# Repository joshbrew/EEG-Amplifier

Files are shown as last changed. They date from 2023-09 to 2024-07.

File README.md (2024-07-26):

## EEG Differential Amplifier

The main circuit here uses 4 low noise op amps to achieve EEG differential amplification. This should plug into any single ended ADC (or put your negative input to ground) to allow even as low as 10 bit EEG.

The amps cost 10 cents from TI, not including the PCB which will vary.

The reference design is for 1000x gain at 5v with a 2.5v voltage reference. All calculations are in the pdf for your needs.

### Resources
- [Differential Amp BOM](https://docs.google.com/spreadsheets/d/1rzFOKtwm5F1gYTblCt51H4664hxHK5iFGmpR6K0Omsg/edit?usp=sharing)
- [Gain Amp BOM](https://docs.google.com/spreadsheets/d/1fu1xdZPcOAWwaKk6sFUOHw02OROvW1wCZvjth2xU8xA/edit?usp=sharing)
- [Design reference](https://github.com/joshbrew/EEG-Amplifier/blob/main/EEG_Active_electrode_design.pdf) by Abishek Parikh. 
Other info pulled from datasheets.

Note my previous OPA202 config was incorrect. And use this formula for calculating the bandpass: 
<table>
  <tr>
    <td>
      <br/>
      In our config, + is our reference <br/> 
      (e.g. ear for EEG or opposite wrist for ECG)
    </td>
    <td>
      
    </td>
    <td>
      Gain = R2 / R1
    </td>
  </tr>
</table>

### OPA4202ID/TL084CDR/TL084OD (or compatible SOIC14) SMT mount.
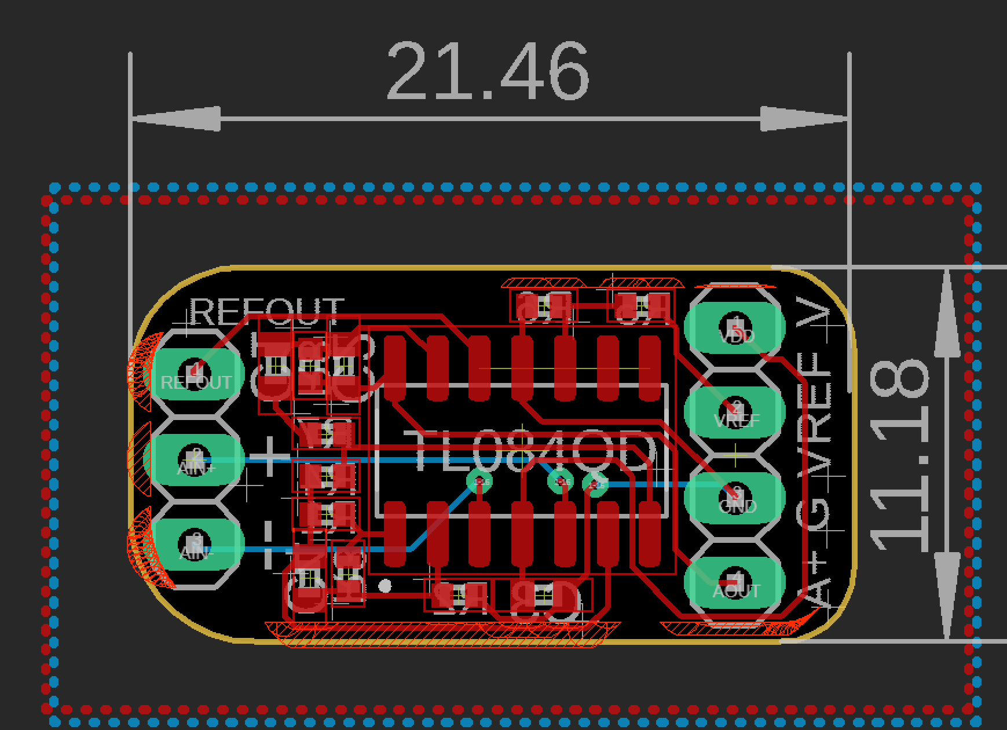
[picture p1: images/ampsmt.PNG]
amp2

OPA4202ID is more expensive but MUCH better quality, with better input impedance (3TΩ) and a 9nV/sqrt(Hz) noise density starting at 0.1Hz. The TL084's spectral noise doesn't bottom out until near 1kHz.

### 4mm Snap Button Electrode Mountholes
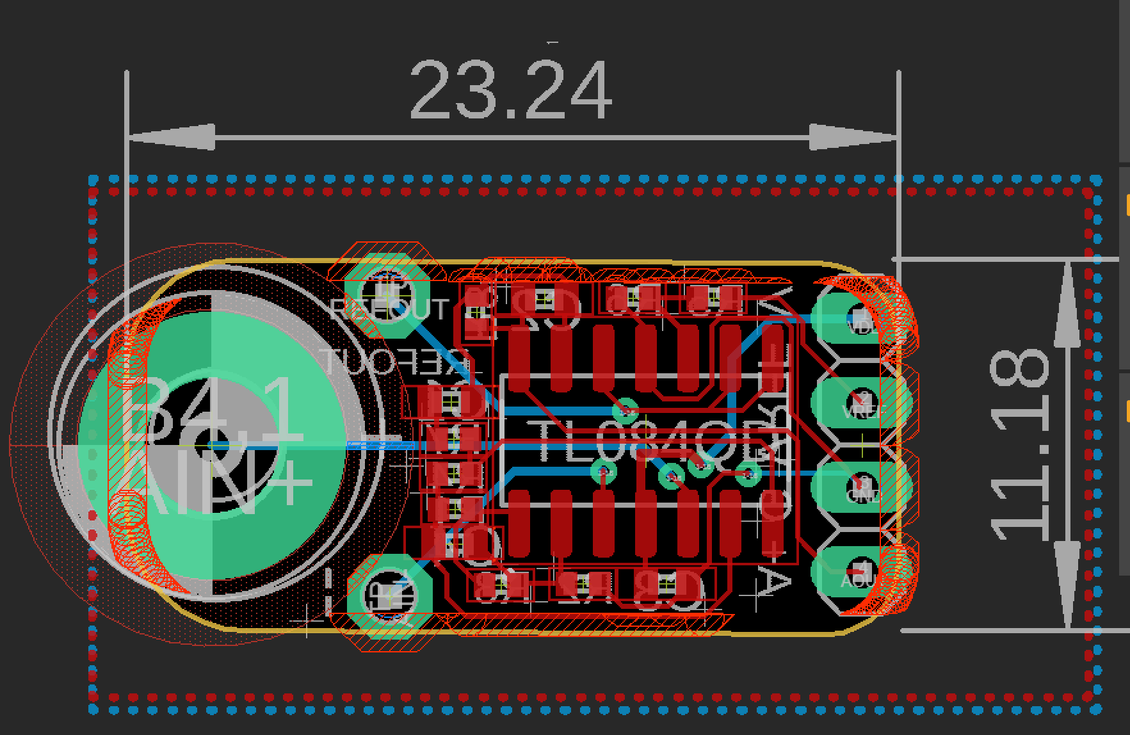
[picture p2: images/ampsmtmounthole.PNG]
amp2mount

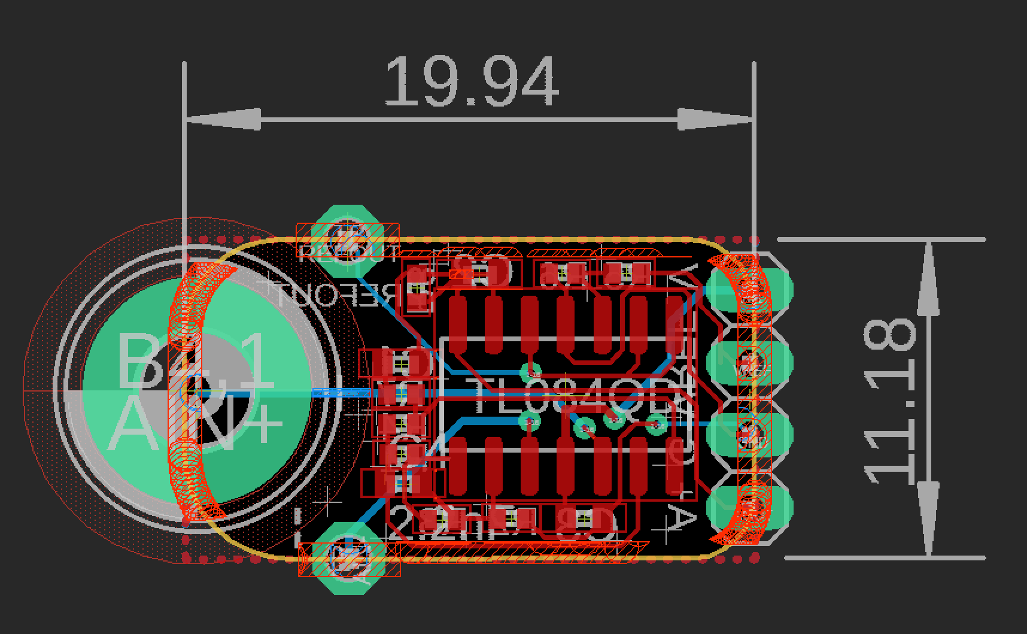
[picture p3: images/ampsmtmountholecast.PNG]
amp2mountCast

Sized for Florida Instruments reusable plastic snap electrodes.

### TL084HCN (A,B,H, etc) Thruhole amp (for DIY)
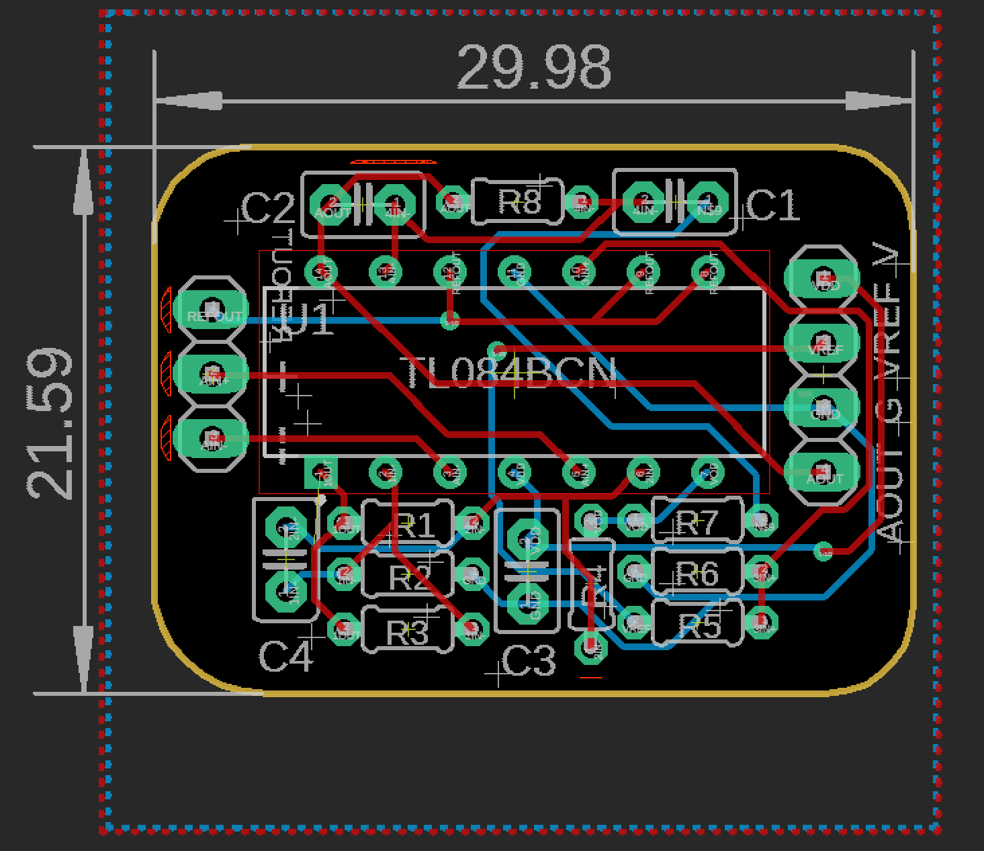
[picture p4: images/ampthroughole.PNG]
amp


### OPA4202IPW or OPA4377 (or  compatible TSSOP14) SMT mount.
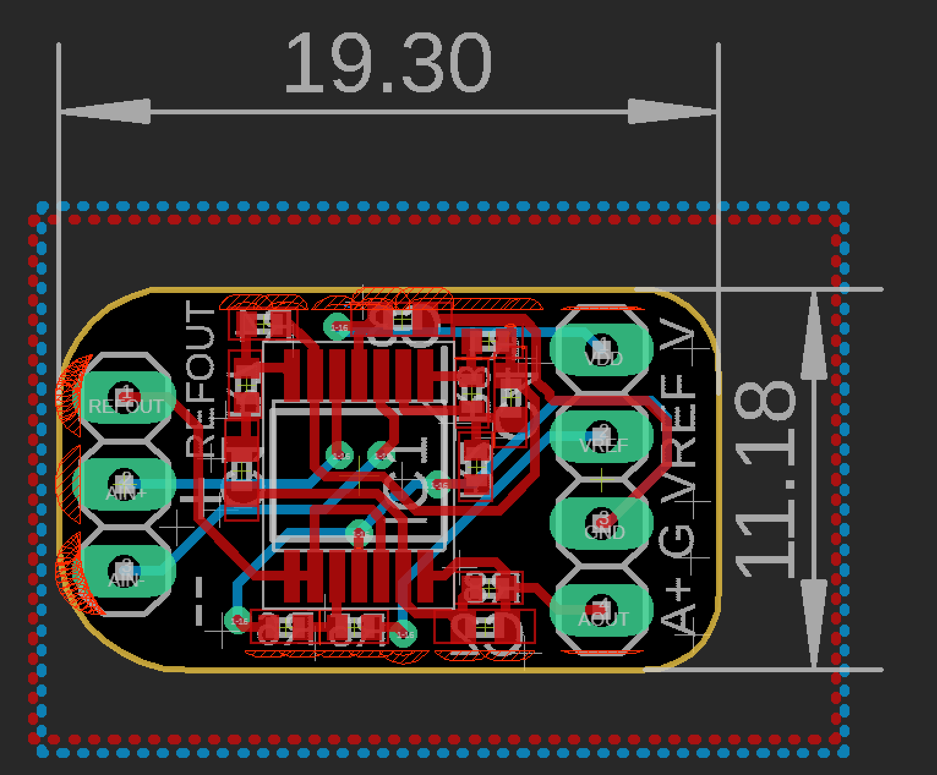
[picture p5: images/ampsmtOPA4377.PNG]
amp3


### Schematics
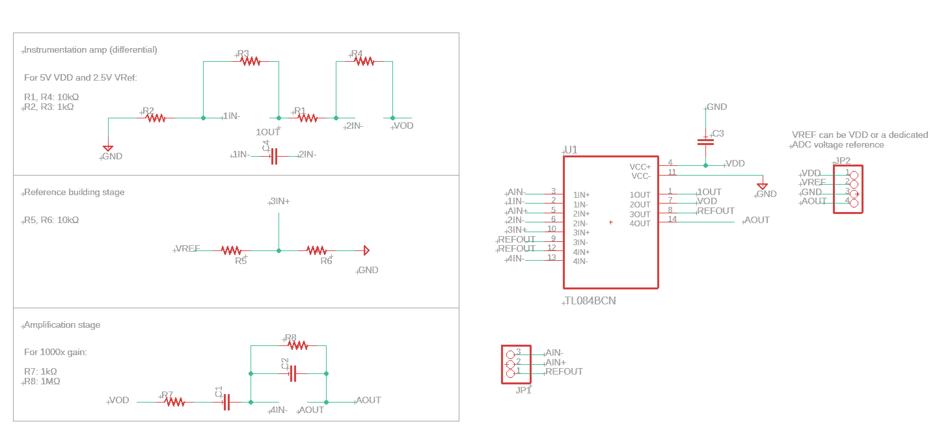
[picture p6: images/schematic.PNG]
schem

The BioAmp EXG Pill has a different layout you can check out. Same chipset.

### Noise vs Measured Bandwidth on OPA4202
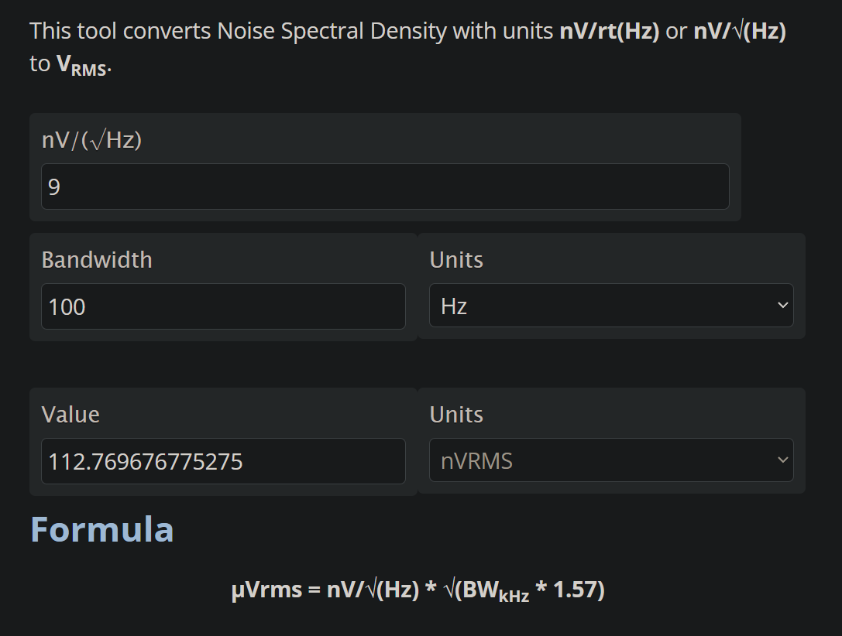
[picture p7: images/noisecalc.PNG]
calcs

Note: Noise calcs are probably inaccurate. Lower frequencies have higher noise density. Adjust bandpass accordingly.

TL084 noise density:
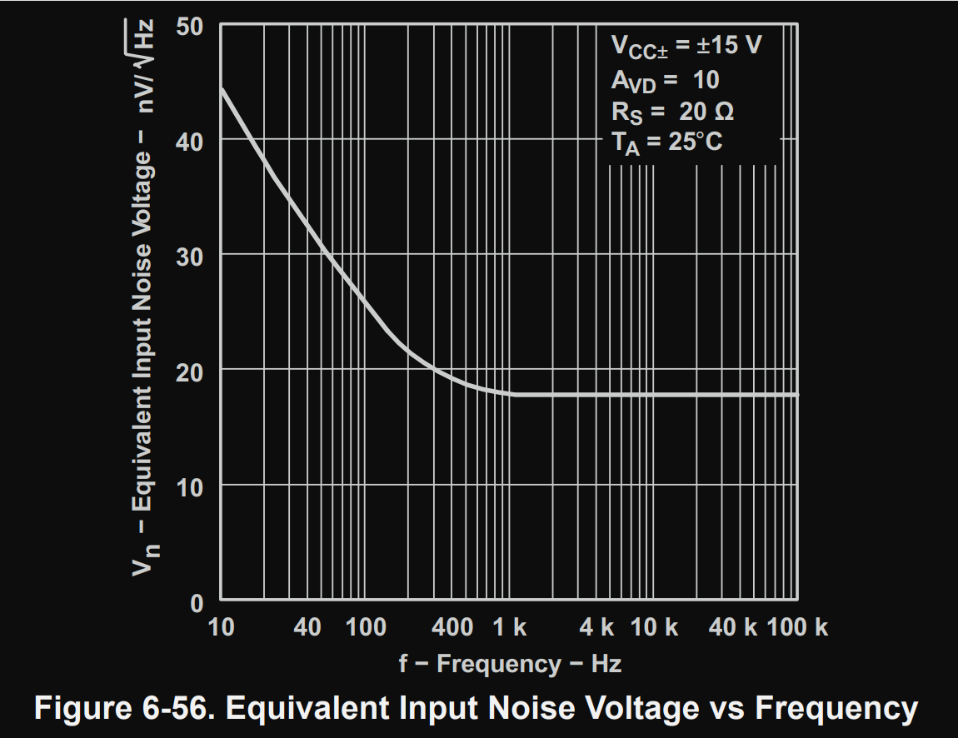
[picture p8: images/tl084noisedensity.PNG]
density


OPA4202 noise density:
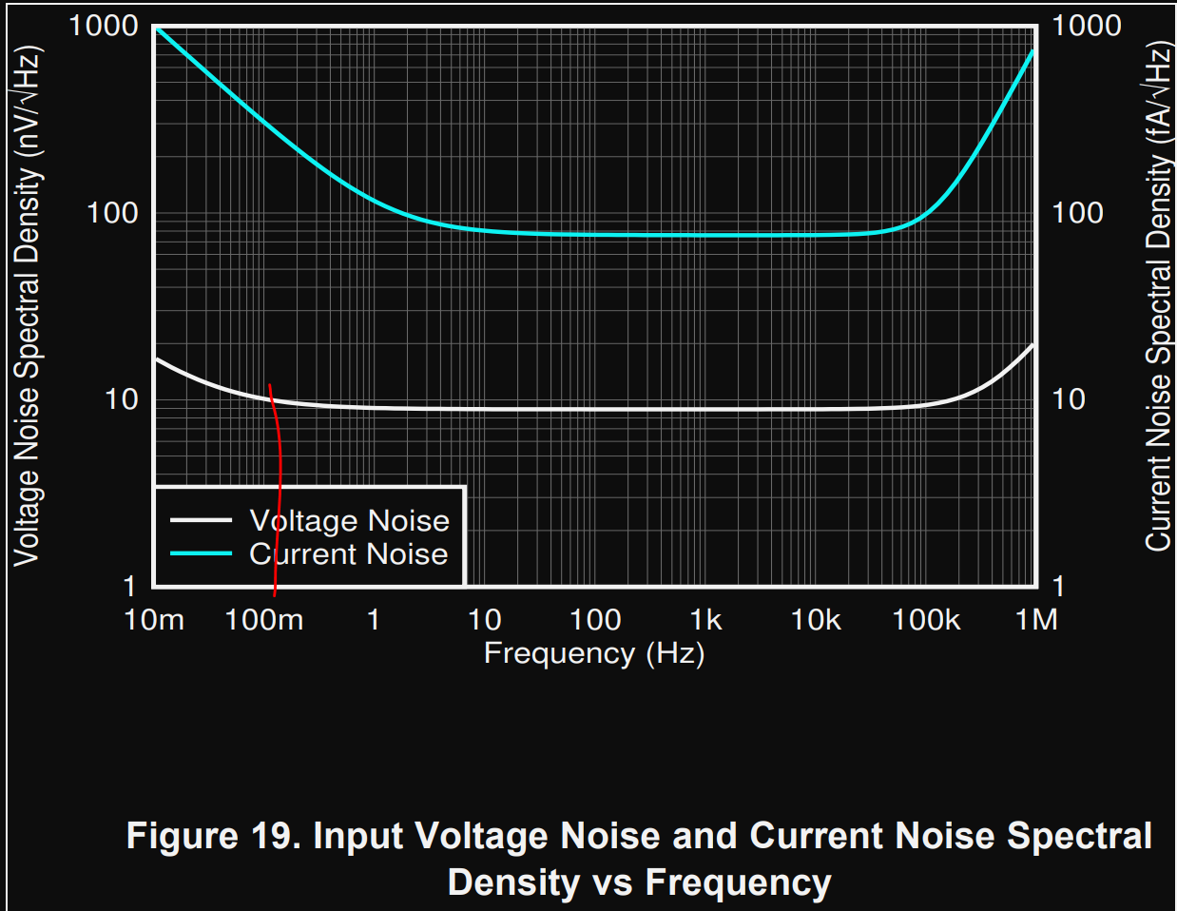
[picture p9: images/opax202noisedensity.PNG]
density2


OPA4202 or OPA4377 are about a dollar. I think the 4202 is better based on the noise.

## Also included in CAD/singular_amps

Single and Dual OPA202/OPA2202 gain amplifiers. E.g. for pre-amplification. Great low frequency noise density. 
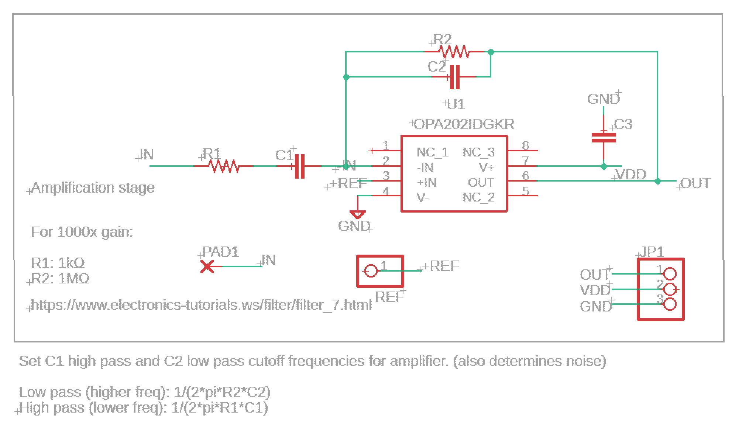
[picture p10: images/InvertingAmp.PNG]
gain


### OPA202 (or pin compatible) VSSOP8 package (or pin compatible)
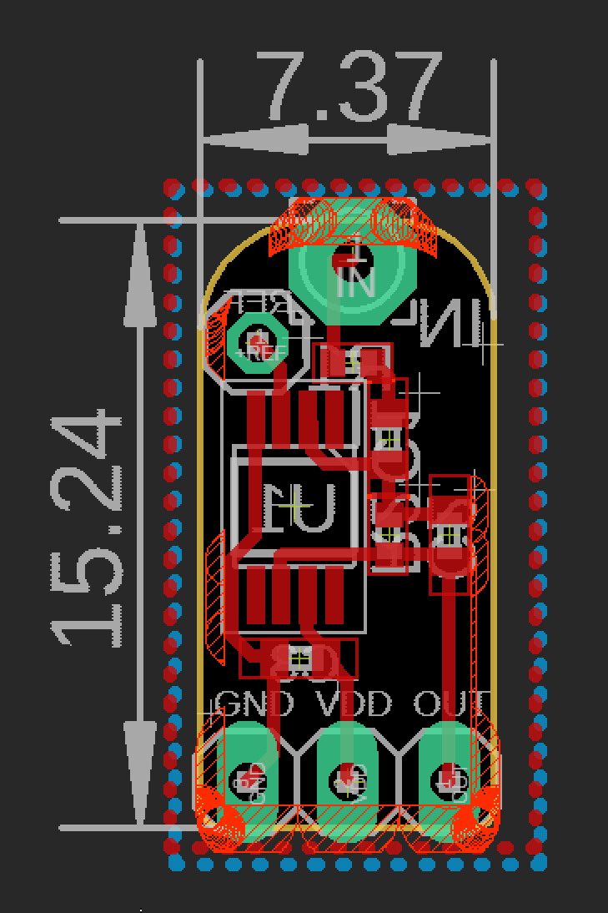
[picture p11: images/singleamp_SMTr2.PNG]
smtgain


### OPA202 VSSOP8 package with 4mm electrode mount
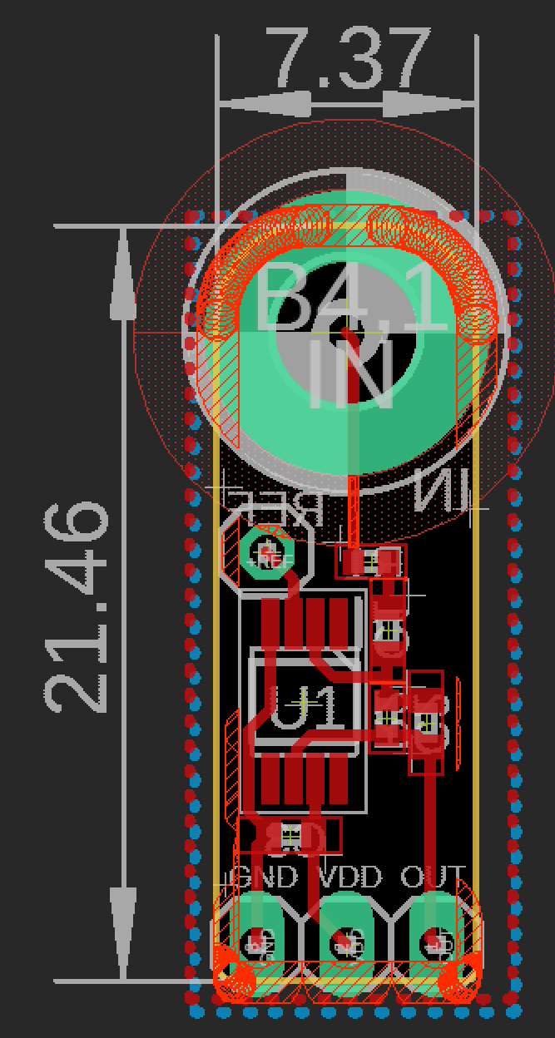
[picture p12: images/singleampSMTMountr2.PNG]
smtgain2


### OPA202 SOIC8 package and thruhole resistors/capacitors (easier to hand solder)
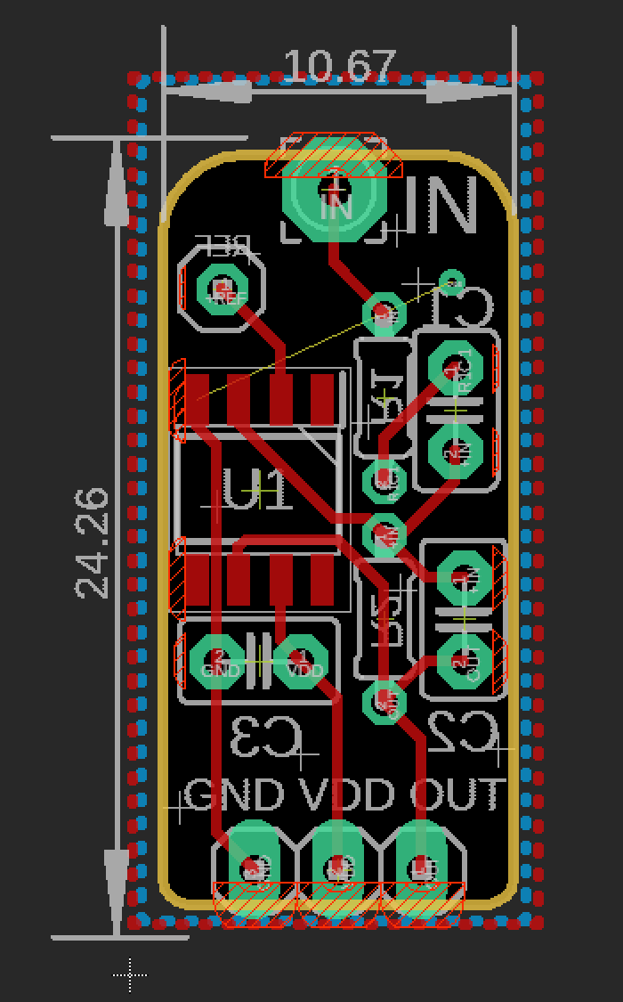
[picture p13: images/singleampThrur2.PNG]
smtgain3


### OPA202 SOIC8 package thruhole with 4mm electrode mount
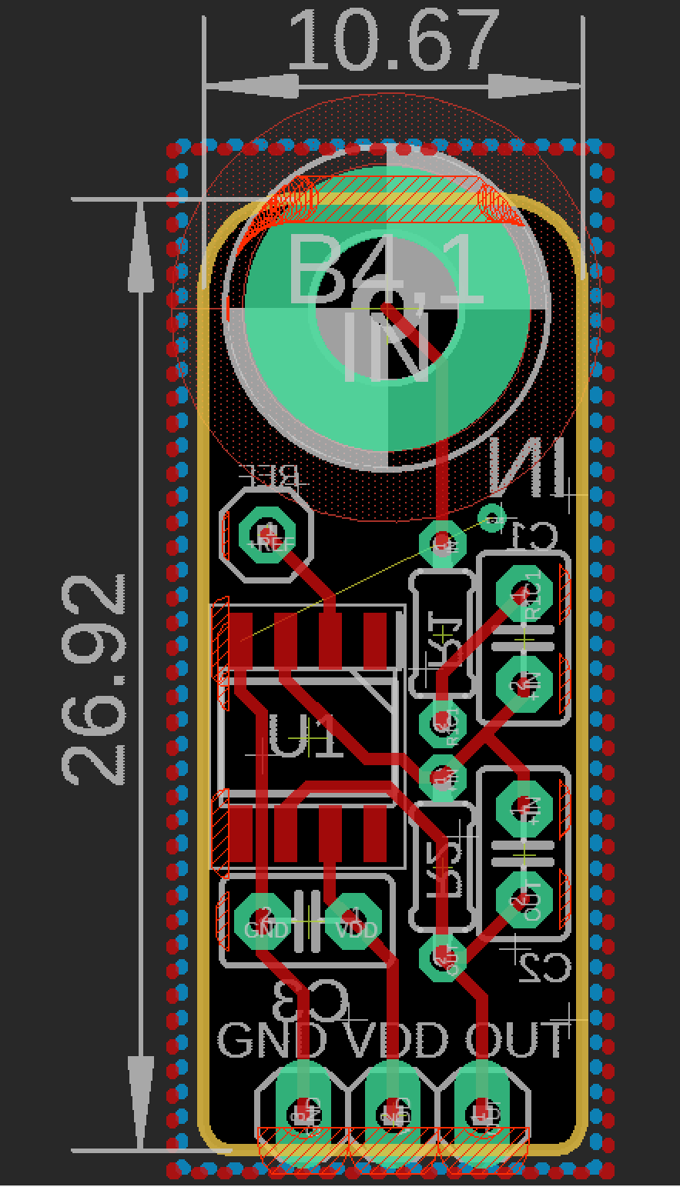
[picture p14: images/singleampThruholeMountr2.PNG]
smtgain4


EAGLE drawings by Josh Brewster. Works in free EAGLE or you can import them elsewhere usually.

Best prices are on TI.com just FYI...

Free source! Definitely question my circuitry before you use it.

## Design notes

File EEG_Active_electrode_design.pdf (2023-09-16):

## Hardware design EEG Amplifier circuit

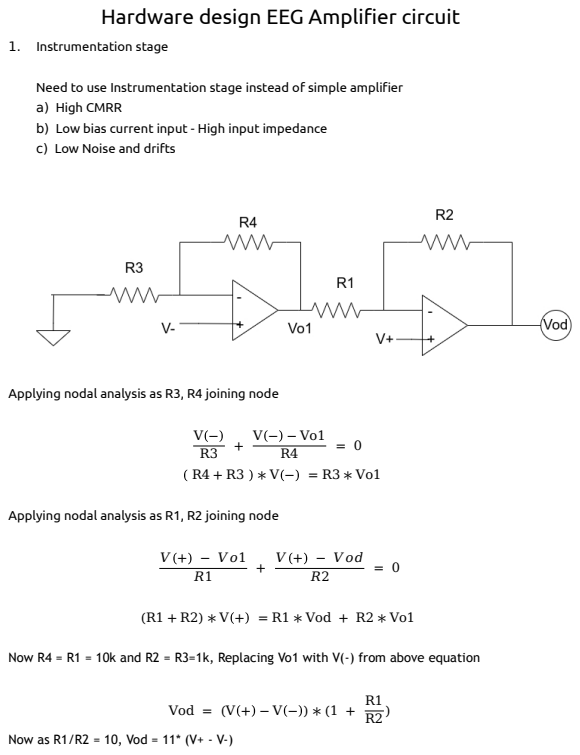
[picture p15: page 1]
1. Instrumentation stage;  + −  2 = 0 (R1 + R2) ∗ V + = R1 ∗ Vod + R2 ∗ Vo1; Vod = (V + − V − ) ∗ (1 +

Need to use Instrumentation stage instead of simple amplifier
a) High CMRR
b) Low bias current input - High input impedance
c) Low Noise and drifts

Applying nodal analysis as R3, R4 joining node

Applying nodal analysis as R1, R2 joining node

Now R4 = R1 = 10k and R2 = R3=1k, Replacing Vo1 with V(-) from above equation

Now as R1/R2 = 10, Vod = 11* (V+ - V-)

2. Reference building stage

Need for reference voltage with

a) Voltage isolation
b) High input impedance
c) Stable reference

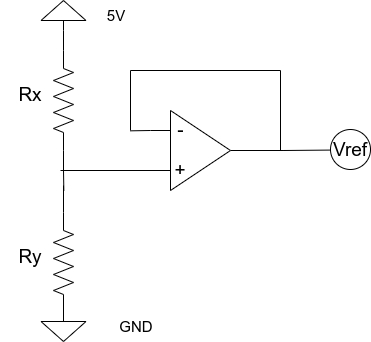
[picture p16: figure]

Here Rx = Ry = 10k
Hence with Unity gain Vref = 2.5 V

We need 2.5V reference as our signal is differential and can go in negative but bias is not negative hence we can get clipped signal

3. Amplification stage

This stage will give gain and hence required here

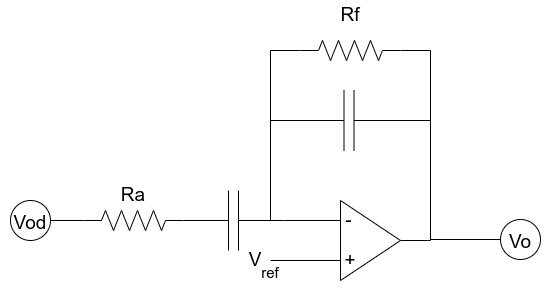
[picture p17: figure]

Here capacitor in series of Ra will block dc signal to flow, Parallel cap to Rf is to filter higher frequencies

Applying nodal at Rf and Ra joint

# Vref − Vd

Ra

+

# Vref − Vo

Rf = 0

# Vo = (Vref ∗

# Rf + Ra

Ra

# ) − (Vin ∗

Rf
Ra

)

Vref term shall be 0 as there’s already a capacitor blocking DC voltages

# Vo = − Vin ∗

Rf
Ra

To get 1000 gain value of Rf = 1M, Ra = 1k
We won’t get 1000x but low as capacitor is there in parallel with Rf and with reduce value it’ll give more gain but it’ll reduce the filtering of higher frequency

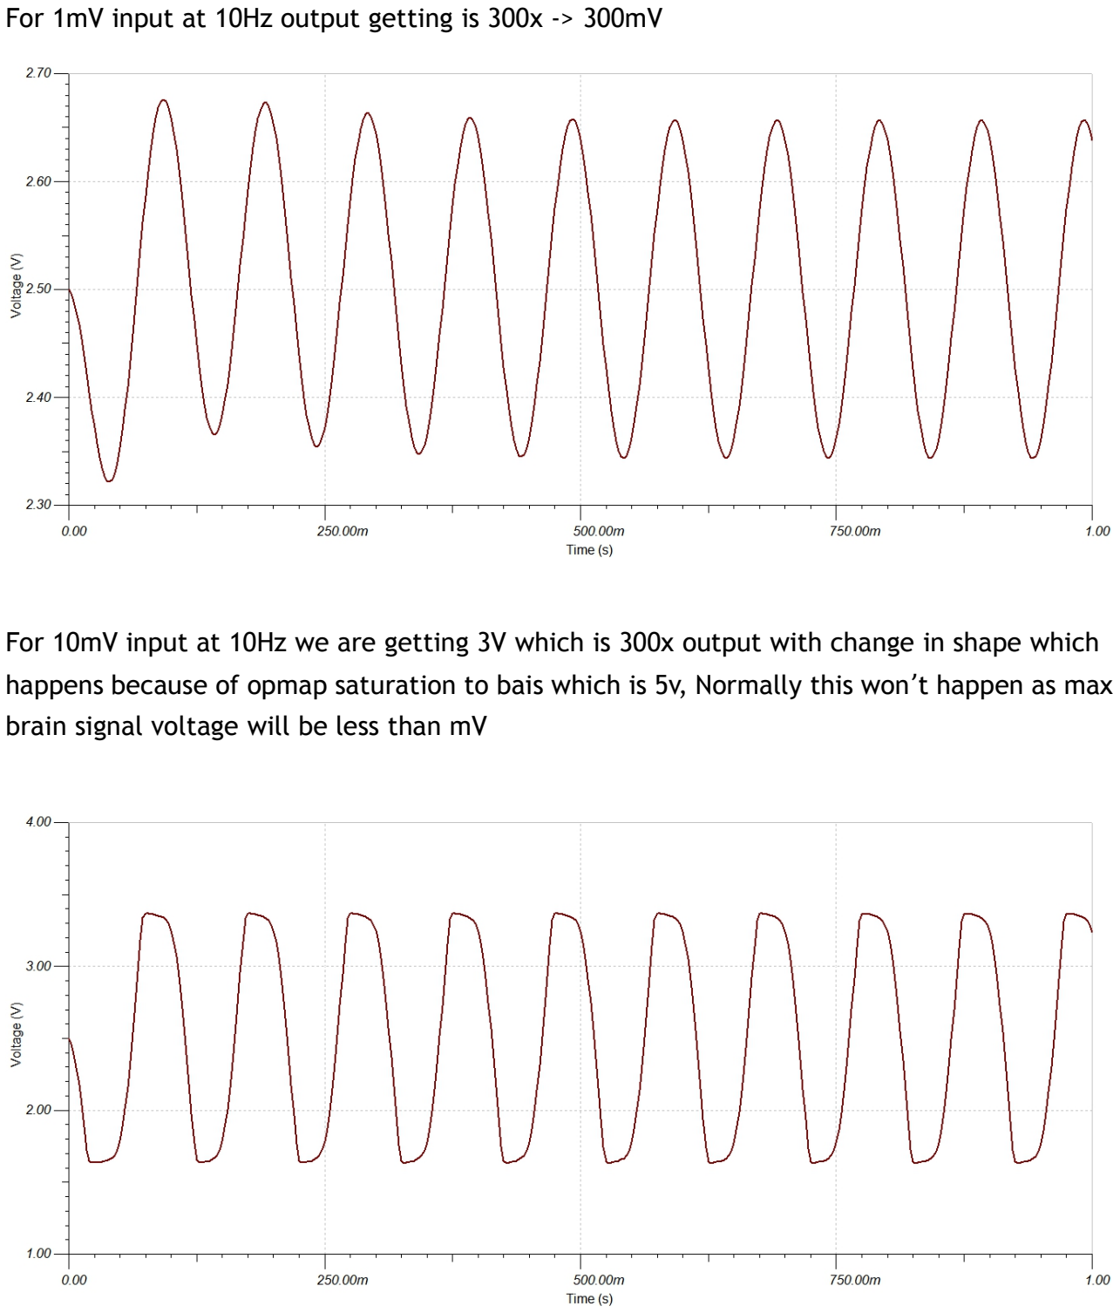
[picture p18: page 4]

For 1mV input at 10Hz output getting is 300x -> 300mV

For 10mV input at 10Hz we are getting 3V which is 300x output with change in shape which happens because of opmap saturation to bais which is 5v, Normally this won’t happen as max

brain signal voltage will be less than mV

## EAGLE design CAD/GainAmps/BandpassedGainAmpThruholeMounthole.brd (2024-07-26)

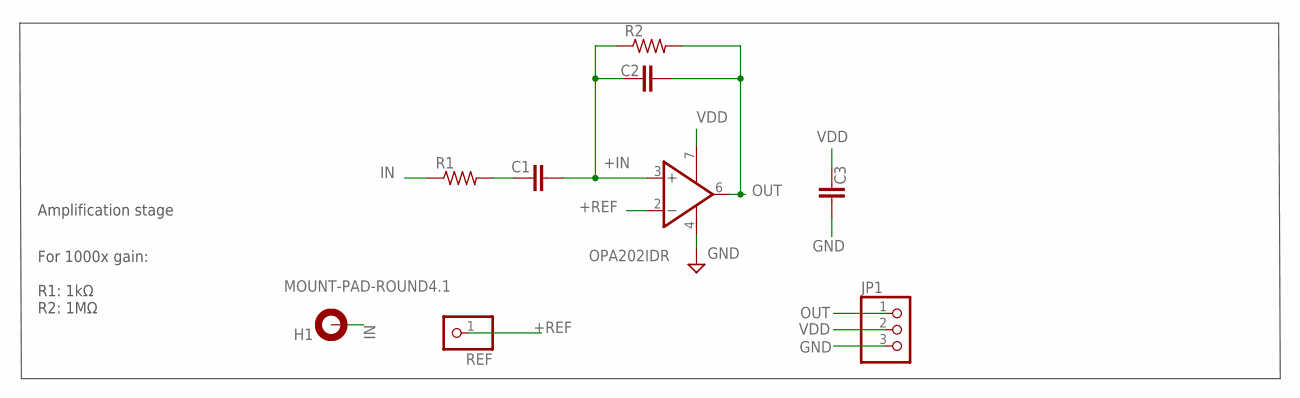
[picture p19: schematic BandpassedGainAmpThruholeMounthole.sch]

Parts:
C1, C2, C3: C2.5/2; C2.5-2
H1: MOUNT-PAD-ROUND4.1; 4,1-PAD
JP1: PINHD-1X3; 1X03
R1, R2: R-US_0204/5; 0204/5
REF: PINHD-1X1; 1X01
U1: OPA202IDR; SOIC127P600X175-8N

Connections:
+IN: C1.2, C2.1, R2.1, U1.3 (+IN)
+REF: REF.1, U1.2 (-IN)
GND: C3.2, JP1.3, U1.4 (V-)
IN: H1.B4,1, R1.1
OUT: C2.2, JP1.1, R2.2, U1.6 (OUT)
R1C1: C1.1, R1.2
VDD: C3.1, JP1.2, U1.7 (V+)

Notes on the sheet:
Amplification stage
For 1000x gain: R1: 1kΩ R2: 1MΩ

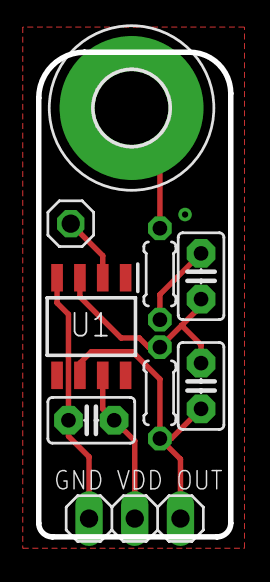
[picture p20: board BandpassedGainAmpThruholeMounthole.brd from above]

Board: 2 copper layers, 10.7 x 26.9 mm, 9 parts (0 on the bottom side), 7 nets.

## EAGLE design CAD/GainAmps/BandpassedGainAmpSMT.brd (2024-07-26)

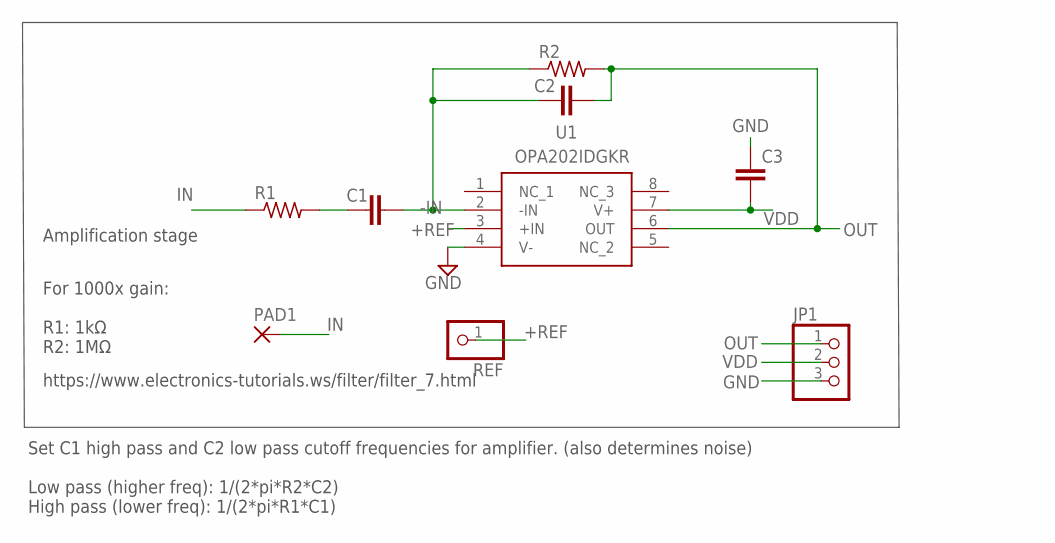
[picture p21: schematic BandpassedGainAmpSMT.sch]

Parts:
C1, C2, C3: C-EUC0402; C0402
JP1: PINHD-1X3; 1X03
PAD1: 3,17/1,1
R1, R2: R-US_R0402; R0402
REF: PINHD-1X1; 1X01
U1: OPA202IDGKR; SOP65P490X110-8N

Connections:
+REF: REF.1, U1.3 (+IN)
-IN: C1.2, C2.1, R2.1, U1.2 (-IN)
GND: C3.1, JP1.3, U1.4 (V-)
IN: PAD1.1, R1.1
OUT: C2.2, JP1.1, R2.2, U1.6 (OUT)
R1C1: C1.1, R1.2
VDD: C3.2, JP1.2, U1.7 (V+)

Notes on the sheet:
Amplification stage
For 1000x gain: R1: 1kΩ R2: 1MΩ
Set C1 high pass and C2 low pass cutoff frequencies for amplifier. (also determines noise) Low pass (higher freq): 1/(2*pi*R2*C2) High pass (lower freq): 1/(2*pi*R1*C1)
https://www.electronics-tutorials.ws/filter/filter_7.html

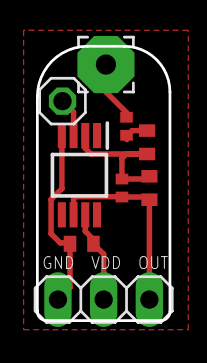
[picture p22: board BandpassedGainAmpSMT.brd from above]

Board: 2 copper layers, 7.4 x 15.2 mm, 9 parts (0 on the bottom side), 7 nets.

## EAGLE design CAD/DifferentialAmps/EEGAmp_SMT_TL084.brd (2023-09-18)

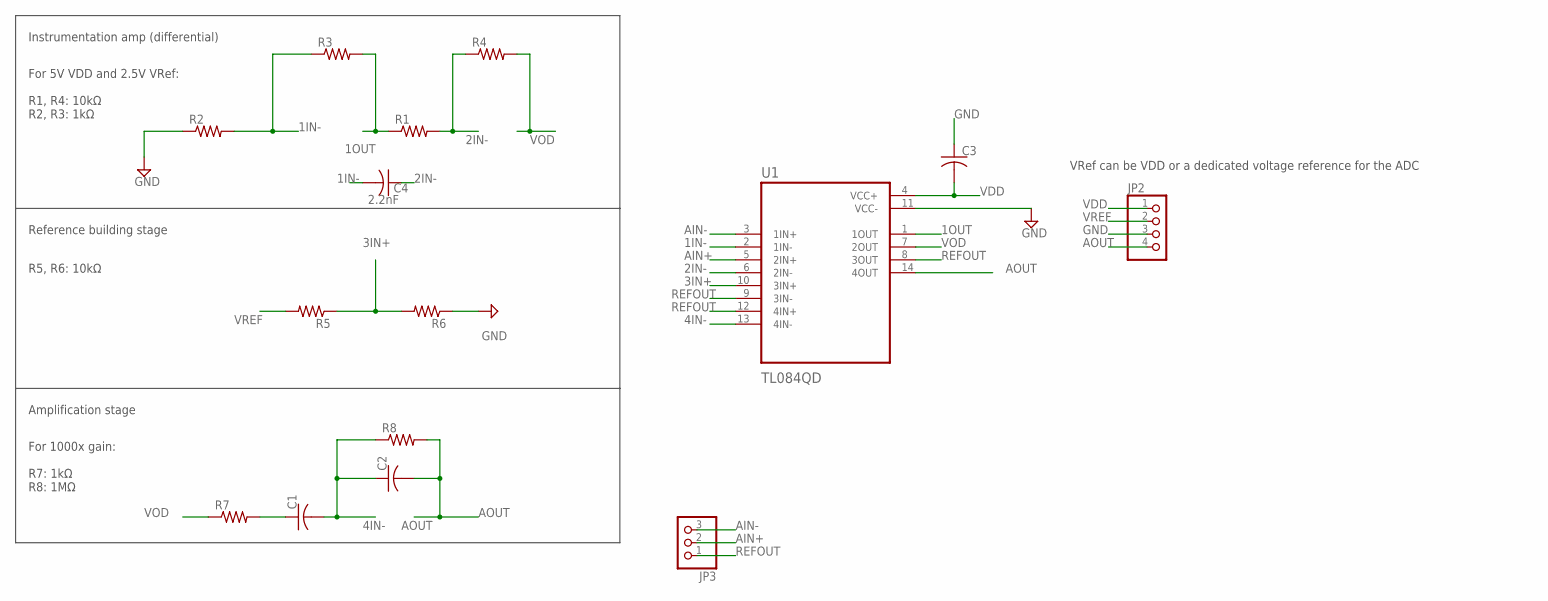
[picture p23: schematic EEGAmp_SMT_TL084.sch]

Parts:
C1, C2, C3: C-USC0402; C0402
C4: 2.2nF; C0402
JP2: PINHD-1X4; 1X04
JP3: PINHD-1X3; 1X03
R1, R2, R3, R4, R5, R6, R7, R8: R-US_R0402; R0402
U1: TL084QD; SOIC127P600X175-14N

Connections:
1IN-: C4.2, R2.2, R3.1, U1.2 (1IN-)
1OUT: R1.1, R3.2, U1.1 (1OUT)
2IN-: C4.1, R1.2, R4.1, U1.6 (2IN-)
3IN+: R5.1, R6.2, U1.10 (3IN+)
4IN-: C1.2, C2.1, R8.1, U1.13 (4IN-)
AIN+: JP3.2, U1.5 (2IN+)
AIN-: JP3.3, U1.3 (1IN+)
AOUT: C2.2, JP2.4, R8.2, U1.14 (4OUT)
GND: C3.1, JP2.3, R2.1, R6.1, U1.11 (VCC-)
unnamed: C1.1, R7.2
REFOUT: JP3.1, U1.8 (3OUT), U1.9 (3IN-), U1.12 (4IN+)
VDD: C3.2, JP2.1, U1.4 (VCC+)
VOD: R4.2, R7.1, U1.7 (2OUT)
VREF: JP2.2, R5.2

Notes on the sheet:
Instrumentation amp (differential)
Reference building stage
Amplification stage
For 5V VDD and 2.5V VRef: R1, R4: 10kΩ R2, R3: 1kΩ
R5, R6: 10kΩ
For 1000x gain: R7: 1kΩ R8: 1MΩ
VRef can be VDD or a dedicated voltage reference for the ADC

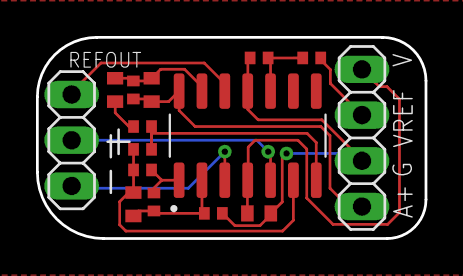
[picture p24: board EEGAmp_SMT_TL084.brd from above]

Board: 2 copper layers, 21.6 x 11.2 mm, 15 parts (0 on the bottom side), 14 nets.

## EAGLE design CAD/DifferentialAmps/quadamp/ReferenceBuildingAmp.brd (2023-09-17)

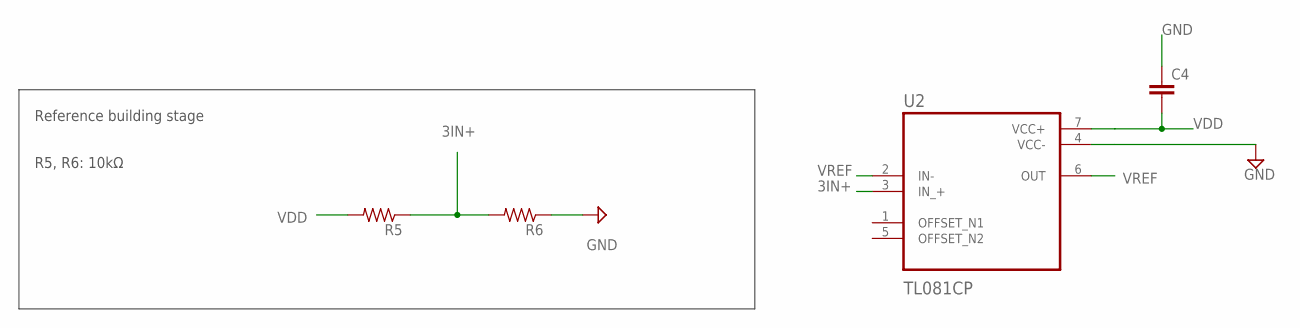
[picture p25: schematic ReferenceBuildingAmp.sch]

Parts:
C4: C2.5/2; C2.5-2
R5, R6: R-US_0204/5; 0204/5
U2: TL081CP; DIP794W45P254L959H508Q8

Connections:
3IN+: R5.1, R6.2, U2.3 (IN_+)
GND: C4.1, R6.1
VDD: C4.2, R5.2
VREF: U2.2 (IN-), U2.6 (OUT)

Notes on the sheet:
Reference building stage
R5, R6: 10kΩ

Board: 2 copper layers, 4 parts (0 on the bottom side), 4 nets, no tracks yet.

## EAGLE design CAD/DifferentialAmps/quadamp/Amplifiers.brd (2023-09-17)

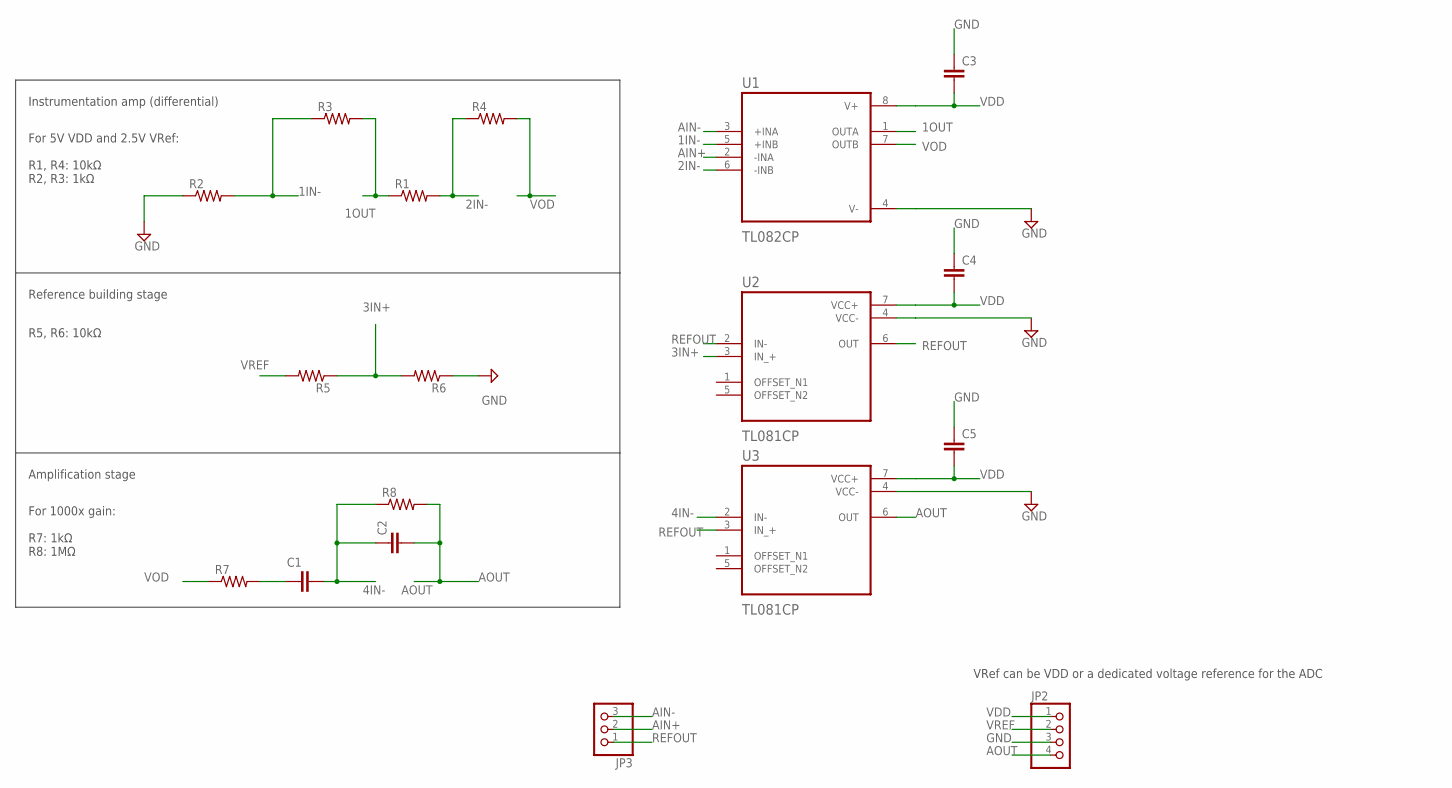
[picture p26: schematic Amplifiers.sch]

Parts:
C1, C2, C3, C4, C5: C2.5/2; C2.5-2
JP2: PINHD-1X4; 1X04
JP3: PINHD-1X3; 1X03
R1, R2, R3, R4, R5, R6, R7, R8: R-US_0204/5; 0204/5
U1: TL082CP; DIP794W45P254L959H508Q8
U2, U3: TL081CP; DIP794W45P254L959H508Q8

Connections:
1IN-: R2.2, R3.1, U1.5 (+INB)
1OUT: R1.1, R3.2, U1.1 (OUTA)
2IN-: R1.2, R4.1, U1.6 (-INB)
3IN+: R5.1, R6.2, U2.3 (IN_+)
4IN-: C1.2, C2.1, R8.1, U3.2 (IN-)
AIN+: JP3.2, U1.2 (-INA)
AIN-: JP3.3, U1.3 (+INA)
AOUT: C2.2, JP2.4, R8.2, U3.6 (OUT)
GND: C3.1, C4.1, C5.1, JP2.3, R2.1, R6.1
unnamed: C1.1, R7.2
REFOUT: JP3.1, U2.2 (IN-), U2.6 (OUT), U3.3 (IN_+)
VDD: C3.2, C4.2, C5.2, JP2.1
VOD: R4.2, R7.1, U1.7 (OUTB)
VREF: JP2.2, R5.2

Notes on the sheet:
Instrumentation amp (differential)
Reference building stage
Amplification stage
For 5V VDD and 2.5V VRef: R1, R4: 10kΩ R2, R3: 1kΩ
R5, R6: 10kΩ
For 1000x gain: R7: 1kΩ R8: 1MΩ
VRef can be VDD or a dedicated voltage reference for the ADC

Board: 2 copper layers, 18 parts (0 on the bottom side), 14 nets, no tracks yet.

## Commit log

2023-09-16 add CAM
    [copper_bottom.gbr, copper_top.gbr, drill_1_16.xln, gerber_job.gbrjob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]
2023-09-16 smt version
    [EEGAmp_SMT.brd, EEGAmp_SMT.sch]
2023-09-16 added mounthole version for integrating a snap electrode. More cam files,
    [EEGAmp_SMT_MountHole.brd, EEGAmp_SMT_MountHole.sch, copper_bottom.gbr, copper_top.gbr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]
2023-09-16 separate castellated mounthole and non castellated, more screenshots/links.
    [EEGAmp_SMT_MountHole_Castellated.brd, EEGAmp_SMT_MountHole_Castellated.sch, copper_bottom.gbr, copper_top.gbr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]
2023-09-16 add centroids
    [EEGAmp_SMT_MountHole_Castellated.brd, EEGAmp_SMT_MountHole_Castellated_centroid.csv, EEGAmp_SMT_MountHole_centroid.csv, EEGAmp_SMT_centroid.csv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]
2023-09-16 fixed, smaller
    [EEGAmp_SMT_MountHole.brd, EEGAmp_SMT_MountHole_Castellated.brd, EEGAmp_SMT_MountHole_Castellated_centroid.csv, EEGAmp_SMT_MountHole_centroid.csv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]
2023-09-16 another wire tolerance fix
    [EEGAmp_SMT_MountHole.brd, copper_top.gbr, drill_1_16.xln, gerber_job.gbrjob]
2023-09-16 and another wire fix
    [EEGAmp_SMT_MountHole.brd, copper_bottom.gbr, drill_1_16.xln, gerber_job.gbrjob]
2023-09-17 fixed reference circuit (oops)
    [EEGAmp_SMT.brd, EEGAmp_SMT.sch, EEGAmp_SMT_MountHole.brd, EEGAmp_SMT_MountHole.sch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]
2023-09-17 readded unfinished single amps w/ fix
    [Amplifiers.brd, Amplifiers.sch, DifferentialAmp.brd, DifferentialAmp.sch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]
2023-09-17 corrected notes
    [Amplifiers.brd, Amplifiers.sch, EEGAmp_SMT.sch, EEGAmp_SMT_MountHole.sch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]
2023-09-18 added a filter cap on inputs
    [EEGAmp_SMT.brd, EEGAmp_SMT.sch, EEGAmp_SMT_MountHole.brd, EEGAmp_SMT_MountHole.sch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]
2023-09-18 add OPA4377 version (still can be made for ~1 dollar)
    [EEGAmp_SMT_OPA4377.brd, EEGAmp_SMT_OPA4377.sch, EEGAmp_SMT_OPA4377_centroid.csv, EEGAmp_SMT_TL084.brd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]
2023-09-18 added a couple non inverting gain amplifiers with bandpass filters
    [Amplifiers.brd, Amplifiers.sch, BandpassedGainAmp.brd, BandpassedGainAmp.sch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]
2023-09-28 finished gain amps
    [BandpassedGainAmpSMT.brd, BandpassedGainAmpSMT.sch, BandpassedGainAmpSMTMounthole.brd, BandpassedGainAmpSMTMounthole.sch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]
2023-09-28 moved, added production files for gain amps
    [Amplifiers.brd, Amplifiers.sch, BandpassedGainAmp.sch, BandpassedGainAmpSMT.brd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]
2023-09-28 fixed edge plating
    [BandpassedGainAmpSMT.brd, BandpassedGainAmpSMT.sch, BandpassedGainAmpSMTMounthole.brd, BandpassedGainAmpSMTMounthole_centroid.csv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]
2024-07-26 fixing bandpass filters soon
